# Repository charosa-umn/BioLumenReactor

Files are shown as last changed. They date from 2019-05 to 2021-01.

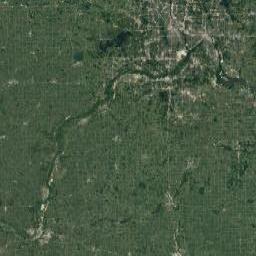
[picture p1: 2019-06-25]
WebPage/Contact_files/embed_data/kh.jpeg

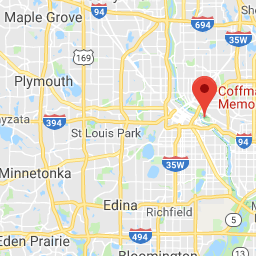
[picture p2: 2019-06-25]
WebPage/Contact_files/embed_data/vt_002.png

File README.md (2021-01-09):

# BioLumen Reactor
The BioLumen Reactor project is dedicated to building a low-cost, small-format bioreactor to culture the bioluminescent bacteria *Vibrio fischeri*. This repository contains open-source code, cell culture protocols, and engineering drawings for the project, and is maintained by **Charosa Research Incubator** at the **University of Minnesota - Twin Cities**.

## Open Source Documentation
- [BioLumen Summary Poster](https://github.com/charosa-umn/BioLumenReactor/blob/master/BioLumen%20Open%20Source%20Files/BioLumen%20Summary%20Poster.pdf)
- [BioLumen Laboratory Manual](https://github.com/charosa-umn/BioLumenReactor/blob/master/BioLumen%20Open%20Source%20Files/BioLumen%20Laboratory%20Manual.pdf)
- [BioLumen Engineering Drawings](https://github.com/charosa-umn/BioLumenReactor/blob/master/BioLumen%20Open%20Source%20Files/BioLumen%20Engineering%20Drawings.pdf)
- [BioLumen Materials List](https://github.com/charosa-umn/BioLumenReactor/blob/master/BioLumen%20Open%20Source%20Files/BioLumen%20Materials%20List.pdf)

## Photos 
BioLumen Reactor
Flask of Vibrio Fischeri

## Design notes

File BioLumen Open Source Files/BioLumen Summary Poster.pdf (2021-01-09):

## Development of a Low-Cost, Small-Format Bioreactor for Bioluminescent Bacterial Cell Culture

David Wang, Conor Sullivan, Joe Herbst, Matthew Landauer, Eric Slaughter, Alex Sweeney Charosa Research Incubator, University of Minnesota

## Introduction

Bioreactors are an essential technology utilized in the production of biologics, fermented products, and specialty chemicals.

[1] Our team seeks to increase exposure to this technology at the undergraduate level. Thus, we have developed a low-cost, small-format bioreactor using nonrestricted materials.
For the demonstration of the bioreactor, the marine bacterium, Vibrio fischeri, was cultured. V. fischeri, which is well-studied for its bioluminescence, is also widely-available for purchase, and is both non-pathogenic and recognized as safe for study in BSL-1 lab spaces.
[2] The bioluminescence of
V. fischeri served crucial for determining inoculation and life cycle timing within the bioreactor system.

## Bioreactor Design

It was critical to the design of the bioreactor that all building materials were widely-available, and that the production of the bioreactor was low-cost in comparison to lab-grade or industrial bioreactors.
The core of the bioreactor is the cell culture vessel, which is a borosilicate glass beaker sealed using a rubber gasket. A magnetic stir plate and stir bar are used to agitate the contents of the vessel. A cylindrical shape for the vessel was chosen for the final design. Initial testing was performed with a round-bottom shape, but issues with stirring turbulence were encountered. The cell culture vessel is modular and can be removed for sterilization separate from the rest of the system. The total volume of the vessel is 1000 mL; considering headspace restrictions during culture, the liquid working volume of the vessel is approximately 500 mL.
The cell-culture vessel is jacketed by a water bath to maintain a consistent temperature. The main structure of the bioreactor system is laser-cut, clear acrylic. Low-cost temperature and pH probes are integrated into the cell culture vessel for real-time monitoring of temperature and pH. A Raspberry Pi 3 microcomputer is used for data output and control of instrumentation.

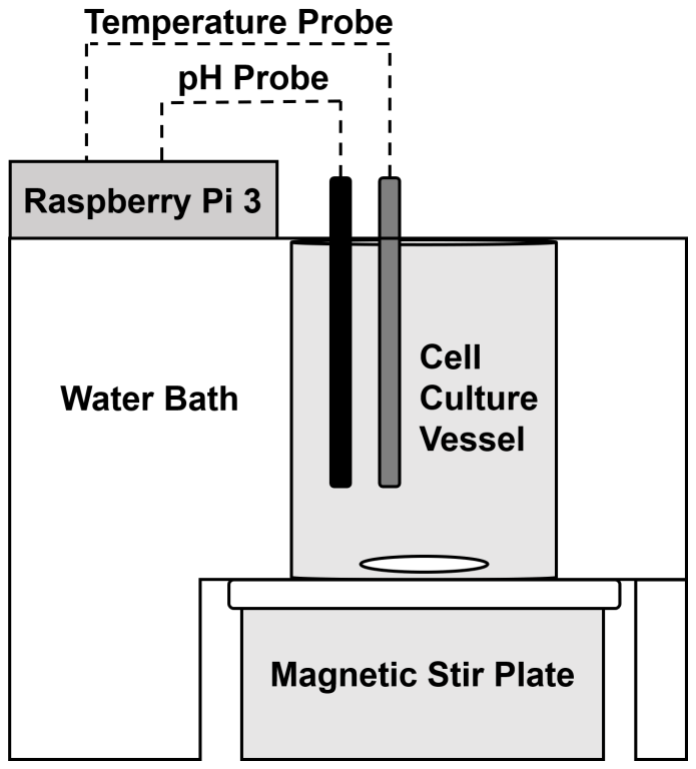
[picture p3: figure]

Figure 1. Final Design Diagram for the Bioreactor

## Cell Culture Methods

The seawater-tryptone nutrient media used for experiments was sourced from the literature and was chosen due to its straightforward composition.

[3] V. fischeri was sourced in the form of educational-grade starter cultures from Carolina Biological Supply Company. Cultures were maintained on solid agar media before scale-up.
For scale-up, 1-2 mL of liquid media was inoculated by a visible cell mass, with 1:10 dilutions of inoculum in fresh nutrient media occurring every 72 hours. Further work to assess scale-up viability was done at the 100 mL scale, with tests done with both shaker platforms and stir plates. Scale-up tests were performed at 22°C, and the target culture pH was approximately 7.2-7.5.
[3] Observed luminescence of the bacteria in culture, which is triggered naturally by cell density, was interpreted as a qualitative indication of both stationary phase growth and of the need for further propagation.

[3]

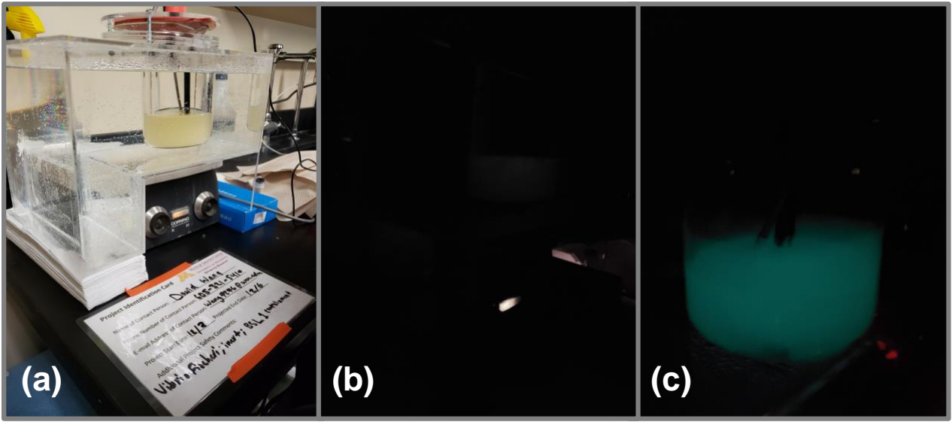
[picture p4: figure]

## Future Directions

- Introduce a heating element for active temperature control; implement a touchscreen and graphical user interface for ease of use
- Pursue other cell culture targets, including hydrogenproducing bacteria, penillicin-producing molds, and cellular viticulture

## Pilot Testing

Test Run 1: The bioreactor was charged with 10% (v/v) inoculum in 500 mL fresh nutrient media. The culture was run for 72 hours. Culture pH and temperature was recorded electronically, but neither parameter was actively controlled. An increase in culture turbidity was observed after 24 hours, but luminescence was not observed during the test run.
Test Run 2: It was suspected that too large of an inoculum volume was used in Test Run 1. Thus, for Test Run 2 the inoculum was reduced to 1% (v/v) in 300 mL fresh nutrient media. The culture was run for 70 hours. After 22 hours the culture turbidity had increased, and after 45 hours luminescence was observed when the culture vessel was shaken.

[1]. Ward, O. P. Bioreactors in Bioprocessing. Bioprocessing 1991, 37–54.
[2]. Ruby et al. Complete Genome Sequence of Vibrio Fischeri: A Symbiotic Bacterium with Pathogenic Congeners. Proc. Natl. Acad. Sci. 2005, 102 (8), 3004–3009. [3]. Madden, D.; Lidesten, B.-M. Bacterial Illumination: Culturing Luminous Bacteria. BioScience Explained 2001.

## References

Figure 2. Test Run 2 at 45 hours: (a) stirred in ambient light,
(b) stirred in total darkness, (c) shaken in total darkness

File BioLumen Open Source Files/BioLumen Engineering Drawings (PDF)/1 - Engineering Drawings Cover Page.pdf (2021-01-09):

# BioLumen Reactor Engineering Drawings

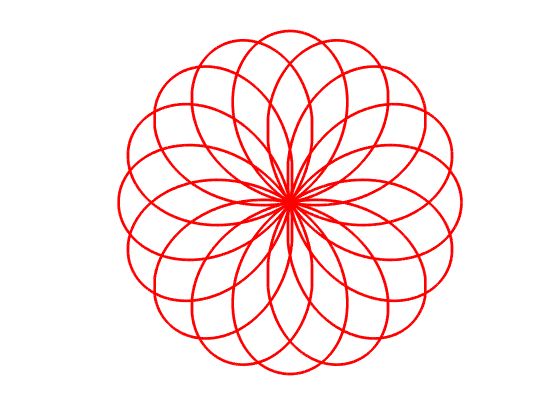
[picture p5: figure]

Author(s): Conor Sullivan
Charosa Research Incubator, University of Minnesota - Twin Cities

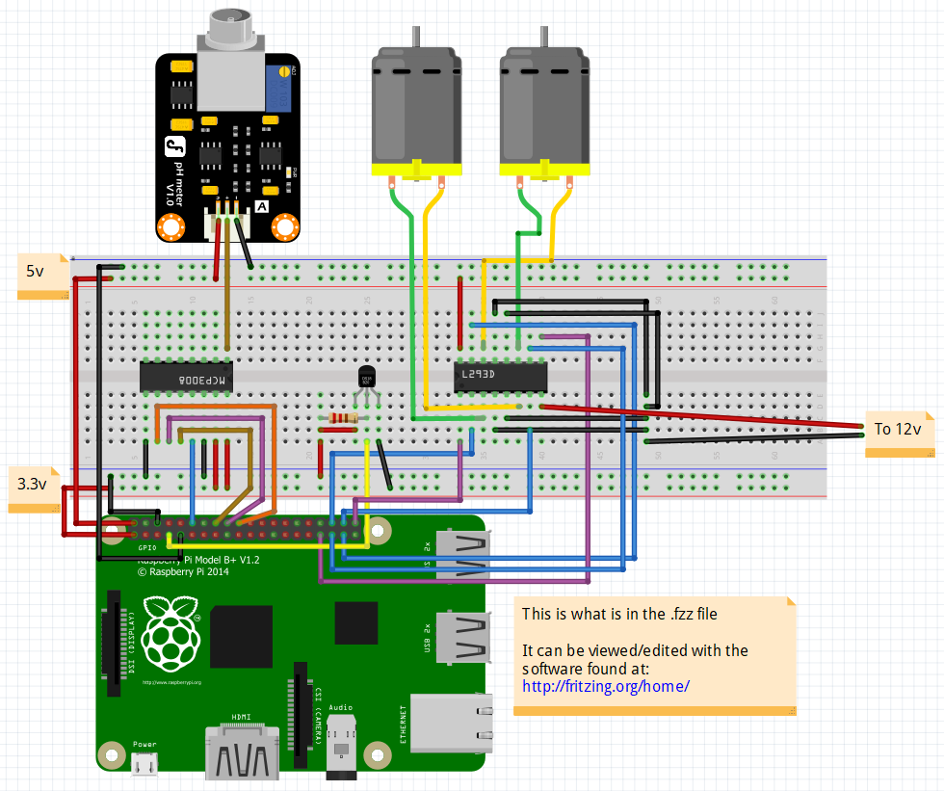
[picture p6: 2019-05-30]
Docs/BoardSchm.png

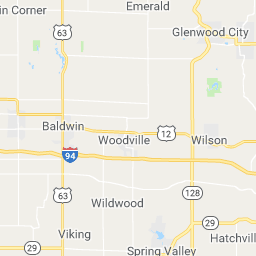
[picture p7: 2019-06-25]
WebPage/Contact_files/embed_data/vt_004.png

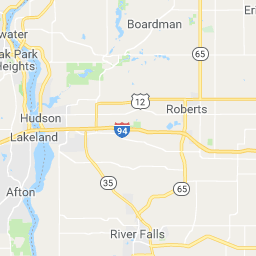
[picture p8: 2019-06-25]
WebPage/Contact_files/embed_data/vt_005.png

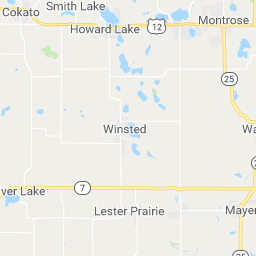
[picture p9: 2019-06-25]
WebPage/Contact_files/embed_data/vt_006.png

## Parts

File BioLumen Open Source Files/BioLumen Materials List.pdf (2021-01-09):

## BioLumen Reactor Materials List

Author(s): David Wang, Conor Sullivan Charosa Research Incubator, University of Minnesota - Twin Cities

Materials for Cell Culture

Item | Recommended Quantity | Preferred Vendor
Magnetic Stir Plate | 1 | eBay
Magnetic Stir Bar | 1 | eBay
Lab Scoopula | 1 | Amazon
Lab Spatula | 1 | Amazon
Digital Milligram Scale | 1 | Amazon
Portable Camp Stove (Flame Source) | 1 | Amazon
Camp Stove Fuel | 1 | Amazon
25 mL Erlenmeyer Flask | 1 | eBay
250 mL Erlenmeyer Flask | 1 | eBay
1 L Media Bottle | 1 | eBay
Plastic Cell Culture Plates | 20 | eBay
Nitrile Gloves | 100 | Amazon
Industrial Spray Bottle | 1 | Amazon
Pressure Cooker | 1 | Amazon
Nichrome Inoculation Loop | 1 | Amazon
Serological Pipette Controller | 1 | eBay

Serological Pipettes | 20 | eBay
Vibrio Fischeri Starter Culture Kit | 1 | Carolina Biological Supply
Yeast Extract | 100 g | Carolina Biological Supply
Seawater Aquarium Salt (‘Instant Ocean’ brand) | 3 lbs | Amazon
Glycerol | 500 mL | Carolina Biological Supply
Tris Base | 250 g | Carolina Biological Supply
Ammonium Chloride | 500 g | Carolina Biological Supply
Tryptone | 500 g | eBay
Calcium Carbonate | 100 g | Carolina Biological Supply
Agar | 100 g | Carolina Biological Supply
Distilled Water | 1 L | Amazon
Ethanol/Isopropanol | 500 mL | Amazon
Clorox Bleach | 1 gal | Amazon

Materials for Construction of Bioreactor

Item | Recommended Quantity | Preferred Vendor
1000 mL Reaction Vessel | 1 | eBay
0.177" thick Acrylic | 32" x 18", 2 sheets | School of Architecture Fab Lab
Acrylic Bonding Agent | 4 oz | Sci-Grip Weld-On 4
Rubber Gasket, ⅛" Thick | 12" x 12", 1 sheet | McMaster Carr, 8525T43
M4x40 Phillips Head BHCS | 4 | -
M4 Wing Nut | 4 | -
Water Heater, 1000 W, 120V | 1 | Denord
Thermocouple/Wire | 1, 3 feet of wire | Amazon
pH sensor | 1 | Amazon
Magnetic Stirrer | 1 | eBay
1" Magnetic Stir Rod | 1 | eBay
Microcontroller | 1 | Raspberry Pi 4

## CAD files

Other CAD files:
BioLumen Open Source Files/BioLumen Engineering Drawings (Source)/ASSY_CLAMPING_RING.iam
BioLumen Open Source Files/BioLumen Engineering Drawings (Source)/ASSY_REACTOR.iam
BioLumen Open Source Files/BioLumen Engineering Drawings (Source)/ASSY_WATER_TANK.iam
BioLumen Open Source Files/BioLumen Engineering Drawings (Source)/BACK_FACE.ipt
BioLumen Open Source Files/BioLumen Engineering Drawings (Source)/BASE.ipt
BioLumen Open Source Files/BioLumen Engineering Drawings (Source)/BOX_SUPPORT.ipt
BioLumen Open Source Files/BioLumen Engineering Drawings (Source)/FRONT_FACE.ipt
BioLumen Open Source Files/BioLumen Engineering Drawings (Source)/GASKET.ipt
BioLumen Open Source Files/BioLumen Engineering Drawings (Source)/GROUND_BASE.ipt
BioLumen Open Source Files/BioLumen Engineering Drawings (Source)/LOWERRING1.ipt
BioLumen Open Source Files/BioLumen Engineering Drawings (Source)/LOWERRING2.ipt
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

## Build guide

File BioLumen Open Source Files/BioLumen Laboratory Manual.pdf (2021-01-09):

## BioLumen Reactor Laboratory Manual

Author(s): David Wang
Charosa Research Incubator, University of Minnesota - Twin Cities

Table of Contents

Introduction | 2
Basic Aseptic Technique for Cell Culture | 3
Alternative Method for Glassware and Reagent Sterilization | 5
Preparation of Photobacterium Liquid and Solid Medium | 7
Subculture of Vibrio Fischeri on Solid Medium | 9
Initiation of Vibrio Fischeri Culture in Liquid Medium | 11
Subculture of Vibrio Fischeri in Liquid Medium | 13
Decontamination of Cell Culture Waste | 15

## Introduction

The goal of the BioLumen Reactor project is to design and build a bioreactor to grow the bioluminescent bacterium Vibrio fischeri. This has required the establishment of multiple laboratory and cell culture protocols that are adaptable to non-standardized working environments, and that are understandable to those with little to no prior laboratory experience. These protocols have been written with reference to prior literature, and also from hands-on experience working with Vibrio fischeri in cell culture. They are also written such that all materials required are non-restricted, and can be freely purchased from sites like eBay, Amazon, and other online retailers.
It is important to note that Vibrio fischeri is a BSL-1 (Biosafety Level 1) organism, meaning it is generally recognized as safe for research, and that it is non-pathogenic to humans. This bacterium exhibits multiple beneficial properties for cell culture, as it is tolerant to a wide range of pH, temperature, and shear conditions in culture. This allows flexibility for culturing at room temperature, with no pH fixing, and with different forms of agitation. It is also commonly used as an educational tool, and so is freely available for purchase at an inexpensive price - in comparison to research-grade strains of bacteria.
This manual represents a year’s worth of laboratory work and literature research by undergraduates at the University of Minnesota - Twin Cities. May it provide you a deeper understanding of cell culture and serve as a future resource for open source science.

David Wang
Project Manager
Charosa Research Incubator

## Basic Aseptic Technique for Cell Culture

Purpose
To remove possible routes of contamination when manipulating cell cultures, and to promote a safe working environment for the cell culturist.

Materials
- Nitrile/latex gloves
- Lab coat (optional)
- Safety glasses (optional)
- Biosafety cabinet (optional)
- Bunsen burner
- 70% ethanol or isopropanol

Procedure
1. Before beginning work, tie long hair up and wash hands thoroughly with soap and water
2. Gown to the appropriate level of personal protective equipment (PPE) for the organism being cultured
a. Gloves are the minimum requirement for PPE
b. Depending on the infection risk of the organism or the necessity for maximum sterility, lab coats, safety glasses or even more stringent PPE may be worn
3. Sterilize the work surface by wiping down thoroughly with 70% ethanol
a. Re-sterilize gloved hands periodically while working with 70% ethanol
b. Similar to Step 2b, a laminar flow hood or biosafety cabinet may be required as an additional layer of protection against contamination and adverse exposure events
c. A non-porous, easily-sterilized work surface in a well-ventilated space is the minimum requirement
4. If working outside of a laminar flow hood or biosafety cabinet, a Bunsen burner can be used to promote a sterile working area (air convection due to flame)
a. Ethanol lamps or butane torches/camp stoves can be used as an alternative to Bunsen burners
b. Avoid rapid gestures when working near a Bunsen burner, and direct coughs or sneezes away from the sterile working area
5. Sterilize any containers or tools that are brought into the sterile area
a. For containers, spray or wipe down openings before use with 70% ethanol
b. For containers, can also ‘flame’ openings before use by slowly moving opening over a Bunsen burner
c. For tools made to be sterilized (glass/steel), can flame sterilize by pouring 95% ethanol over and burning vapors off over a Bunsen burner d. For inoculation loops (nickel/chrome), can flame sterilize directly in a Bunsen burner until glowing orange
e. Let 10 seconds pass after flame sterilizing a tool before use, and do not bring tool into contact with non-sterile surfaces in the interim
6. When finished working, re-sterilize the work surface with 70% ethanol and wash hands thoroughly with soap and water

References
1. Coté, R. Aseptic Technique For Cell Culture. Current Protocols in Cell Biology 1998, 00 (1), 1.3.1-1.3.10.
2. Cell Culture Protocol 1: Proper Aseptic Technique and Sterile Handling of Cells. https://www.sigmaaldrich.com/technical-documents/protocols/biology/aseptic-technique. html (accessed Aug 17, 2020).

## Alternative Method for Glassware and Reagent Sterilization

Purpose
To ensure that all glassware, media, and other components that come into contact with a culture are properly sterilized before use.

Materials
- Pressure Cooker or Autoclave (recommended)
- Liquid Medium/Agar/Glassware to sterilize

Procedure
1. If using an autoclave, see manufacturer instructions for most accurate guidance.
a. Generally use a ‘liquid cycle’ if available for liquid media
b. For agar/agarose gels, cycle times > 20 minutes are recommended
c. Do not fill your container more than half of its total volume with liquid, to prevent over-pressurization
d. Ensure a layer of secondary containment when autoclaving, i.e. an autoclave-safe tray or bin
e. For vessels or bottles filled with liquid, make sure caps are screwed on loosely, to prevent over-pressuring the container
f. It is recommended to use autoclave tape on the vessel of interest, which changes color to ensure that the autoclave reached the proper temperature
2. If using a pressure cooker, set so as to maintain 15 psi for > 15 minutes
a. An inch or two of water in the pressure cooker vessel is necessary for steam pressurization
b. Set containers offset from the bottom of the pressure cooker vessel, to prevent overheating
c. Do not fill your container more than half of its total volume with liquid, to prevent overpressurization
d. For vessels or bottles filled with liquid, make sure caps are screwed on loosely, to prevent over-pressuring the container
e. It is recommended to let steam vent naturally, rather than directly releasing steam via a pressure cooker’s depressurization valve after a pressure cycle
f. A foil cap, taped over the container can be substituted if a vessel does not have a built-in cap
3. After sterilizing a container, do not open or expose its contents unless in a sterile environment
a. Either a biosafety cabinet, laminar flow hood, or sterile field provided by a Bunsen burner

References
1. Teach.Genetics. 2015. Sterilizing Liquids. [online] Available at: <https://teach.genetics.utah.edu/content/microbiology/liquids/> [Accessed 19 August 2020].
2. Swenson, V.; Stacy, A.; Gaylor, M.; Ushijima, B.; Philmus, B.; Cozy, L.; Videau, N.; Videau, P. Assessment And Verification Of Commercially Available Pressure Cookers For Laboratory Sterilization. PLOS ONE 2018, 13 (12), e0208769.

## Preparation of Photobacterium Liquid and Solid Medium

Purpose
To prepare both liquid and solid growth medium for the culture of Vibrio fischeri or other photobacterium.

Materials
- Seawater aquarium salt (33 g/L)
- Yeast extract (5 g/L)
- Tryptone (5 g/L)
- Glycerol (3 g/L, ~2.5–3 mL)
- Tris (6 g/L)
- NH4Cl (5 g/L)
- Distilled water
- CaCO3 (1 g/L, for solid medium)
- Agar (15–20 g/L, for solid medium)
- Erlenmeyer flask/media bottle
- Plastic cell culture plates or sterile glass petri dishes (for solid medium)
Procedure
1. Measure the required solids for liquid medium, and transfer to a suitable container for autoclaving and pouring (Erlenmeyer flask/media bottle)
a. If preparing solid medium, measure the additional solids, CaCO3 and agar, to supplement the liquid recipe
2. Dissolve the solids in the desired volume of distilled water, and add liquid glycerol
a. Small amount of solids may not completely dissolve at room temperature, can move forward if solution is nearly clear
3. Autoclave or pressure sterilize, a cycle time > 20 minutes is recommended
a. See ‘Alternative Method for Glassware and Reagent Sterilization’
4. Allow solution to cool to a manageable temperature, ~15-20 minutes
a. If preparing liquid medium, once cooled can store refrigerated for 3-4 weeks or longer if kept sterile
5. If preparing solid medium, set up a sterile work area to pour agar plates
a. See ‘Basic Aseptic Technique for Cell Culture’, Steps 1-4
6. Pour plates within the sterile work area
a. Set plates on sterile work surface and pour agar down from container
b. Keep one hand free to move plate lids, and use the other to pour liquid agar from the container
c. Only need to pour enough to cover the bottom of the plate
d. Replace place lid, slightly askew, after pouring agar
e. Allow excess steam to be released, ~15-20 minutes, before properly closing plate lids and storing plates f. Store plates upside down, agar-side up, to prevent condensation forming on the agar surface
g. Can store plates either in plastic-wrapped stacks or in the plastic sleeves that they originally came in
h. Plates can be stored refrigerator for 3-4 weeks or longer if kept sterile, and if the agar has not dried out
7. Re-sterilize the work area and work tools; clear the work area and put away items used for the procedure

References
1. Madden, D. and Lidesten, B., 2001. Bacterial Illumination. [online] Available at: <https://bioenv.gu.se/digitalAssets/1566/1566430_photoen.pdf> [Accessed 24 August 2020].
2. Making Agar Plates. https://teach.genetics.utah.edu/content/microbiology/plates/(accessed Aug 24, 2020).

## Subculture of Vibrio Fischeri on Solid Medium

Purpose
To promote the aseptic subculturing of Vibrio fischeri from a starter culture on solid medium to another solid medium.

Materials
- Inoculation loop
- Starter culture, on agar slant/plate
- Bunsen burner or alternative
- 70% ethanol
- Photobacterium agar plate

Procedure
1. Prepare a sterile work area with the Bunsen burner and by wiping down work surfaces with 70% ethanol
a. See Basic Aseptic Technique for Cell Culture, Steps 1-4
2. Move all containers and working items into the sterile work area
a. See Basic Aseptic Technique for Cell Culture, Step 5
3. Flame sterilize inoculation loop in Bunsen burner before contact with any culture
a. See Basic Aseptic Technique for Cell Culture, Step 5
4. Work carefully, using one hand to manipulate the inoculation loop, and one hand to manipulate the cell cultures
5. Rub inoculation loop over an area of the starter culture surface with visible bacteria growth
a. Can look like white or yellow ‘plaques’ on the agar
b. Can confirm if the visible areas are Vibrio fischeri growth by viewing them in a dark room to check bioluminescence - should glow blue-green
6. Without touching the inoculated loop to any other surface, rub the loop onto the surface of the fresh agar plate
a. Recommended technique is to ‘streak’ from center to rim of the plate
b. Very little force is necessary to streak the plate with the inoculation loop, be careful not to tear the agar
c. See Reference 1 for more information on plating techniques
7. Label plate lid with a Sharpie or other indelible marker, noting the date of subculture, the organism name, the type of medium, and the name of the cell culturist
8. Let plate incubate at the appropriate temperature, light intensity, and humidity
a. For Vibrio fischeri, average room temperature (~22° C) or slightly below is an appropriate temperature, and store in a dark, dry space to incubate
9. Re-sterilize the work area and work tools; clear the work area and put away items used for the procedure

10. Depending on how effective the inoculation from the starter culture was, bioluminescence of the culture on solid medium can be observed after ~24 hours
a. Observe in a dark room, and give time for eyesight to adjust to the dark before viewing

References
1. Sanders, E. Aseptic Laboratory Techniques: Plating Methods. Journal of Visualized Experiments 2012, No. 63.

## Initiation of Vibrio Fischeri Culture in Liquid Medium

Purpose
To promote the aseptic subculturing of Vibrio fischeri from a starter culture on solid medium to liquid medium.

Materials
- Inoculation loop
- Starter culture, on agar slant/plate
- Bunsen burner or alternative
- 70% ethanol
- Photobacterium liquid medium
- Cell culture flask (Shake flask/Erlenmeyer flask)
- Magnetic stir plate/shaker platform
- Magnetic stir bar

Procedure
1. Prepare a sterile work area with the Bunsen burner and by wiping down work surfaces with 70% ethanol
a. See Basic Aseptic Technique for Cell Culture, Steps 1-4
2. Move all containers and working items into the sterile work area
a. See Basic Aseptic Technique for Cell Culture, Step 5
3. Flame sterilize inoculation loop in Bunsen burner before contact with any culture
a. See Basic Aseptic Technique for Cell Culture, Step 5
4. Prepare the cell culture flask (sterilized shake/Erlenmeyer flask) by filling with liquid medium
a. If using a magnetic stir plate, insert a magnetic stir bar into the cell culture flask
b. If using an Erlenmeyer flask without a lid, use a metal foil cap (secured with tape) to cover the opening before taking the flask out of the sterile region
c. Do not fill the cell culture flask beyond half of its indicated volume, to ensure excess oxygen headspace for the culture
d. The smaller the volume of media, the faster it will take for the seed culture of Vibrio fischeri to deplete the media of nutrients and begin to die off; 15-20 mL of liquid media for the initiation is recommended
5. Work carefully, using one hand to manipulate the inoculation loop, and one hand to manipulate the cell cultures
6. Rub inoculation loop over an area of the starter culture surface with visible bacteria growth
a. Can look like white or yellow ‘plaques’ on the agar
b. Can confirm if the visible areas are Vibrio fischeri growth by viewing them in a dark room to check bioluminescence - should glow blue-green c. To ensure enough transfer of cells, scrape enough cells to notice visually from the surface of the plate
7. Without touching the inoculated loop to any other surface, insert the loop below the liquid surface of the cell culture flask and swirl/shake the loop to inoculate the medium with seed cells
a. Swirling the inoculation loop in the liquid medu only requires ~15 seconds
b. If a visible cell mass was scraped from the starter culture, shake until dislodged from the inoculation loop
8. Reseal the cell culture flask, and incubate at the appropriate temperature, light intensity, and humidity on either a magnetic stir plate or shaker platform
a. For Vibrio fischeri, average room temperature (~22° C) or slightly below is an appropriate temperature, and store in a dark, dry space to incubate
b. To determine a proper agitation rate for shaker or stir plate in the case that the culture was inoculated with a visible cell mass, choose a high enough rate to visibly rotate the cell mass at > 1/second.
9. Re-sterilize the work area and work tools; clear the work area and put away items used for the procedure
10. Depending on the volume of media in the cell culture flask and how large the inoculation mass was, bioluminescence of the liquid culture can be observed after ~24 hours, and can be induced by shaking the culture flask, assuming excess oxygen headspace for the culture
a. Observe in a dark room, and give time for eyesight to adjust to the dark before viewing

References
1. Christensen, D. and Visick, K., 2020. Vibrio fischeri : Laboratory Cultivation, Storage, and Common Phenotypic Assays. Current Protocols in Microbiology, 57(1).
2. Living Organism Care Guide: Vibrio fischeri. https://www.carolina.com/teacher-resources/Interactive/living-organism-care-guide-vibrio-fischeri/tr23902.tr (accessed Aug 29, 2020).

## Subculture of Vibrio Fischeri in Liquid Medium

Purpose
To promote the aseptic subculturing of Vibrio fischeri from a starter culture in liquid medium to another liquid medium.

Materials
- Serological pipette/pipette gun
- Starter culture, in liquid medium
- Bunsen burner or alternative
- 70% ethanol
- Photobacterium liquid medium
- Cell culture flask (Shake flask/Erlenmeyer flask)
- Magnetic stir plate/shaker platform
- Magnetic stir bar (if using stir plate)

Procedure
1. Prepare a sterile work area with the Bunsen burner and by wiping down work surfaces with 70% ethanol
a. See Basic Aseptic Technique for Cell Culture, Steps 1-4
2. Move all containers and working items into the sterile work area
a. See Basic Aseptic Technique for Cell Culture, Step 5
3. Prepare the cell culture flask (sterilized shake/Erlenmeyer flask) by filling with liquid medium
a. If using a magnetic stir plate, insert a magnetic stir bar into the cell culture flask
b. If using an Erlenmeyer flask without a lid, use a metal foil cap (secured with tape) to cover the opening before taking the flask out of the sterile region
c. Do not fill the cell culture flask beyond half of its indicated volume, to ensure excess oxygen headspace for the culture
d. The chosen volume of liquid medium for the subculture vessel depends on multiple factors:
i. If expansion of the cell culture is desired, the entire starter culture can be transferred into a much larger volume of fresh cell culture media
ii. | If the total volume of the culture is meant to be conserved, a fractional
| volume of the starter culture can be transferred into a proportional volume
| of fresh cell culture media
iii. | A volume ratio of 1:100 starter culture to fresh media is recommended for
| cell culture expansion, to maintain ~3 day growth cycle
4. Using a serological pipette and pipette gun, transfer the intended volume of active culture from the starter culture flask to the fresh medium flask
a. Before transferring liquid from the starter culture flask to the serological pipette, swirl the flask to resuspend and homogenize the cells in the culture medium b. Do not contaminate the outer surface of the serological pipette by touching to any other surface while transferring the cell culture liquid
c. If a serological pipette and pipette gun is not available, it is possible to pour starter culture liquid from one flask to another; however, this increases the risk of contamination by the surrounding air, and increases the risks of spills
5. Reseal the new cell culture flask, and incubate at the appropriate temperature, light intensity, and humidity on either a magnetic stir plate or shaker platform
a. For Vibrio fischeri, average room temperature (~22° C) or slightly below is an appropriate temperature, and store in a dark, dry space to incubate
b. To determine a proper agitation rate for shaker or stir plate in the case that the culture was inoculated with a visible cell mass, choose a high enough rate to visibly rotate the cell mass at > 1/second.
6. Re-sterilize the work area and work tools; clear the work area and put away items used for the procedure
7. Depending on the volume of media in the cell culture flask and how large the inoculation volume was, bioluminescence of the liquid culture can be observed after ~24 hours, and can be induced by shaking the culture flask, assuming excess oxygen headspace for the culture
a. Observe in a dark room, and give time for eyesight to adjust to the dark before viewing

References
1. Christensen, D. and Visick, K., 2020. Vibrio fischeri : Laboratory Cultivation, Storage, and Common Phenotypic Assays. Current Protocols in Microbiology, 57(1).
2. Living Organism Care Guide: Vibrio fischeri. https://www.carolina.com/teacher-resources/Interactive/living-organism-care-guide-vibrio-fischeri/tr23902.tr (accessed Aug 29, 2020).

## Decontamination of Cell Culture Waste

Purpose
To safely decontaminate and dispose of cell culture wastes - most importantly, spent cell culture medium used for the growth of Vibrio fischeri.

Materials
- Clorox Bleach (NaOCl)
- Cell Culture Waste
- Autoclave (or equivalent)

Procedure
1. For decontamination of cell cultures in liquid medium with bleach, dilute until flask contains 10% bleach by volume
a. If possible, perform decontamination procedure within a fume hood or other well-vented area
b. Allow at least 20 minutes of contact time for bleach in solution to inactivate any cells left in the culture
c. Can dispose of decontaminated solution via drain disposal, flushed down with copious amounts of water
2. For decontamination of cell cultures on solid medium with bleach, can prepare a solution of 10% bleach in water in a large bin
a. Submerge cell culture plates, or other solid growth media fully under bleach solution
b. Allow at least 20 minutes of contact time for bleach in solution to inactivate any cells left in the culture
c. Can dispose of decontaminated solids as biohazard waste in accordance with institutional or local guidelines
3. For decontamination of cell cultures in liquid or solid medium in an autoclave or equivalent:
a. Place cell culture flasks/plates in a leakproof, autoclave-safe bin
b. Ensure that any containers with liquid are no more than half full
c. Autoclave as recommended by machine instructions; see Alternative Method for Glassware and Reagent Sterilization for more information
d. Can dispose of decontaminated liquids via drain disposal, flushed down with copious amounts of water
e. Can dispose of decontaminated solids as biohazard waste in accordance with institutional or local guidelines

References
1. COMS Policy on Suitable Methods of Liquid Decontamination and Disposal. https://hms.harvard.edu/departments/committee-microbiological-safety/registering-coms/coms-policies/coms-policy-suitable-methods-liquid-decontamination-disposal (accessed Aug 31, 2020).
2. COMS Policy on Suitable Methods of Liquid Decontamination and Disposal. https://hms.harvard.edu/departments/committee-microbiological-safety/registering-coms/coms-policies/coms-policy-suitable-methods-liquid-decontamination-disposal (accessed Aug 31, 2020).

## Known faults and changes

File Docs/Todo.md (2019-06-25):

### TODO List for BioLumen

Things that need to be decided/done:

- [x] What we will use for the controller
- [x] What language we will be using
- [x] Board schimatic
- [x] What sensors we will need
- [x] Set up temp reading
- [x] Convert volatage from digital to pH
- [x] Writting to csv
- [x] Write to realtime webpage
- [x] Display realtime graph
- [x] Begin after button press
- [x] Prep routine
- [ ] Run on startup
- [ ] Get data file to mounted flashdrive
- [ ] Calibrating pH sensor
- [ ] Power down when off switch is activated
- [ ] Begin prep when on switch is activated
- [ ] Documentation requirements

Items that we WILL need:
- [x] RaspberryPi
- [x] Resistors
- [x] Thermometer sensor
- [x] ph sensor
- [x] Breadboard
- [x] Pump for acids and bases
- [ ] Wires
- [ ] PCB board
- [ ] On/off switch
- [ ] Push button

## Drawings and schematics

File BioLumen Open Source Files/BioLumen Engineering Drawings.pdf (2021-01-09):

# BioLumen Reactor Engineering Drawings


Author(s): Conor Sullivan
Charosa Research Incubator, University of Minnesota - Twin Cities

1

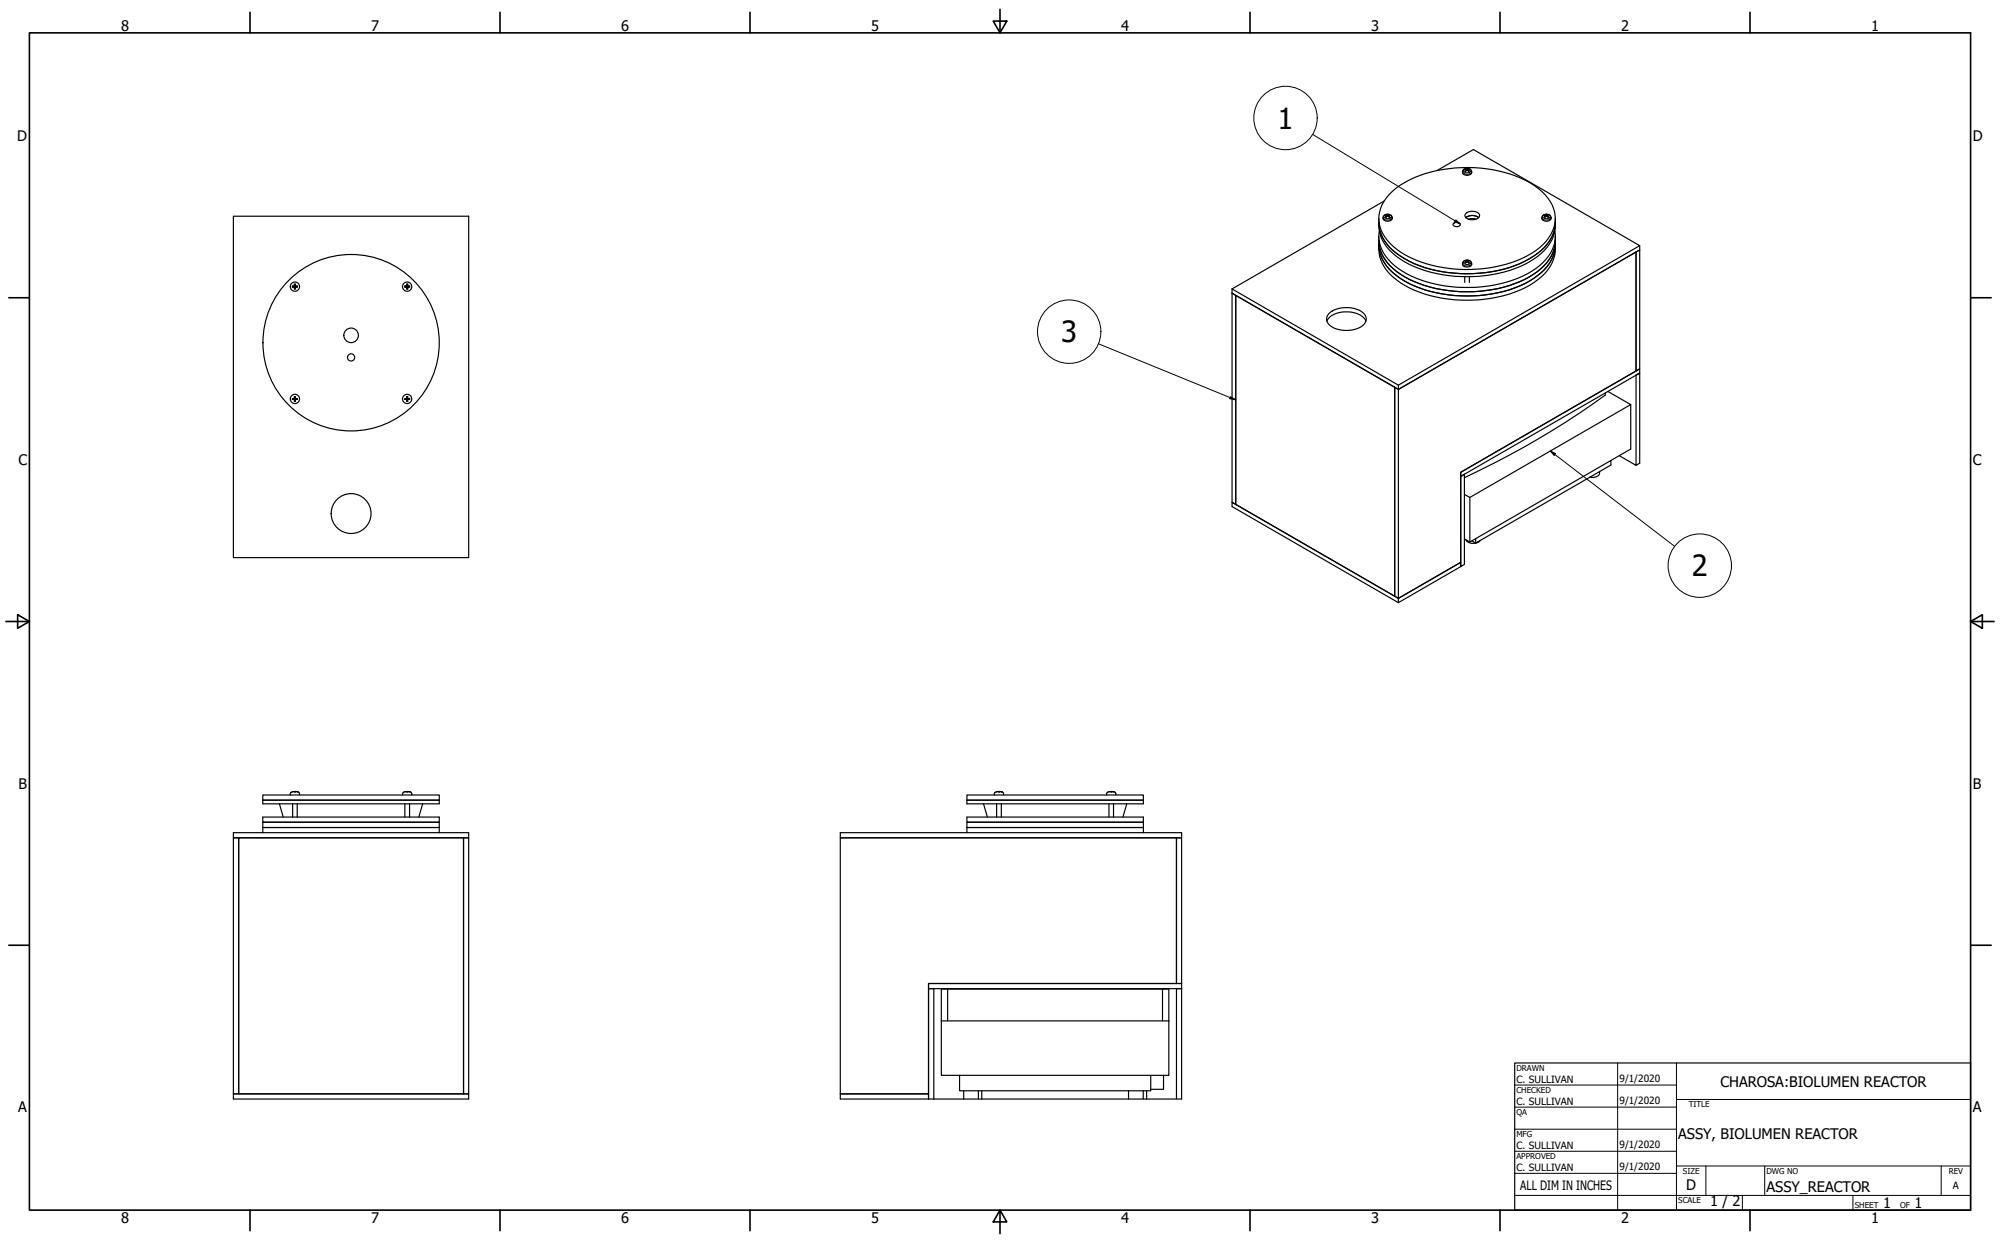
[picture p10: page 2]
SHEET 1 OF 1; DRAWN; CHECKED; C. SULLIVAN; DWG NO; ASSY_REACTOR; TITLE; SIZE D; SCALE; REV A

CHAROSA:BIOLUMEN REACTOR

ASSY, BIOLUMEN REACTOR

MFG
C. SULLIVAN
APPROVED
ALL DIM IN INCHES

3

6

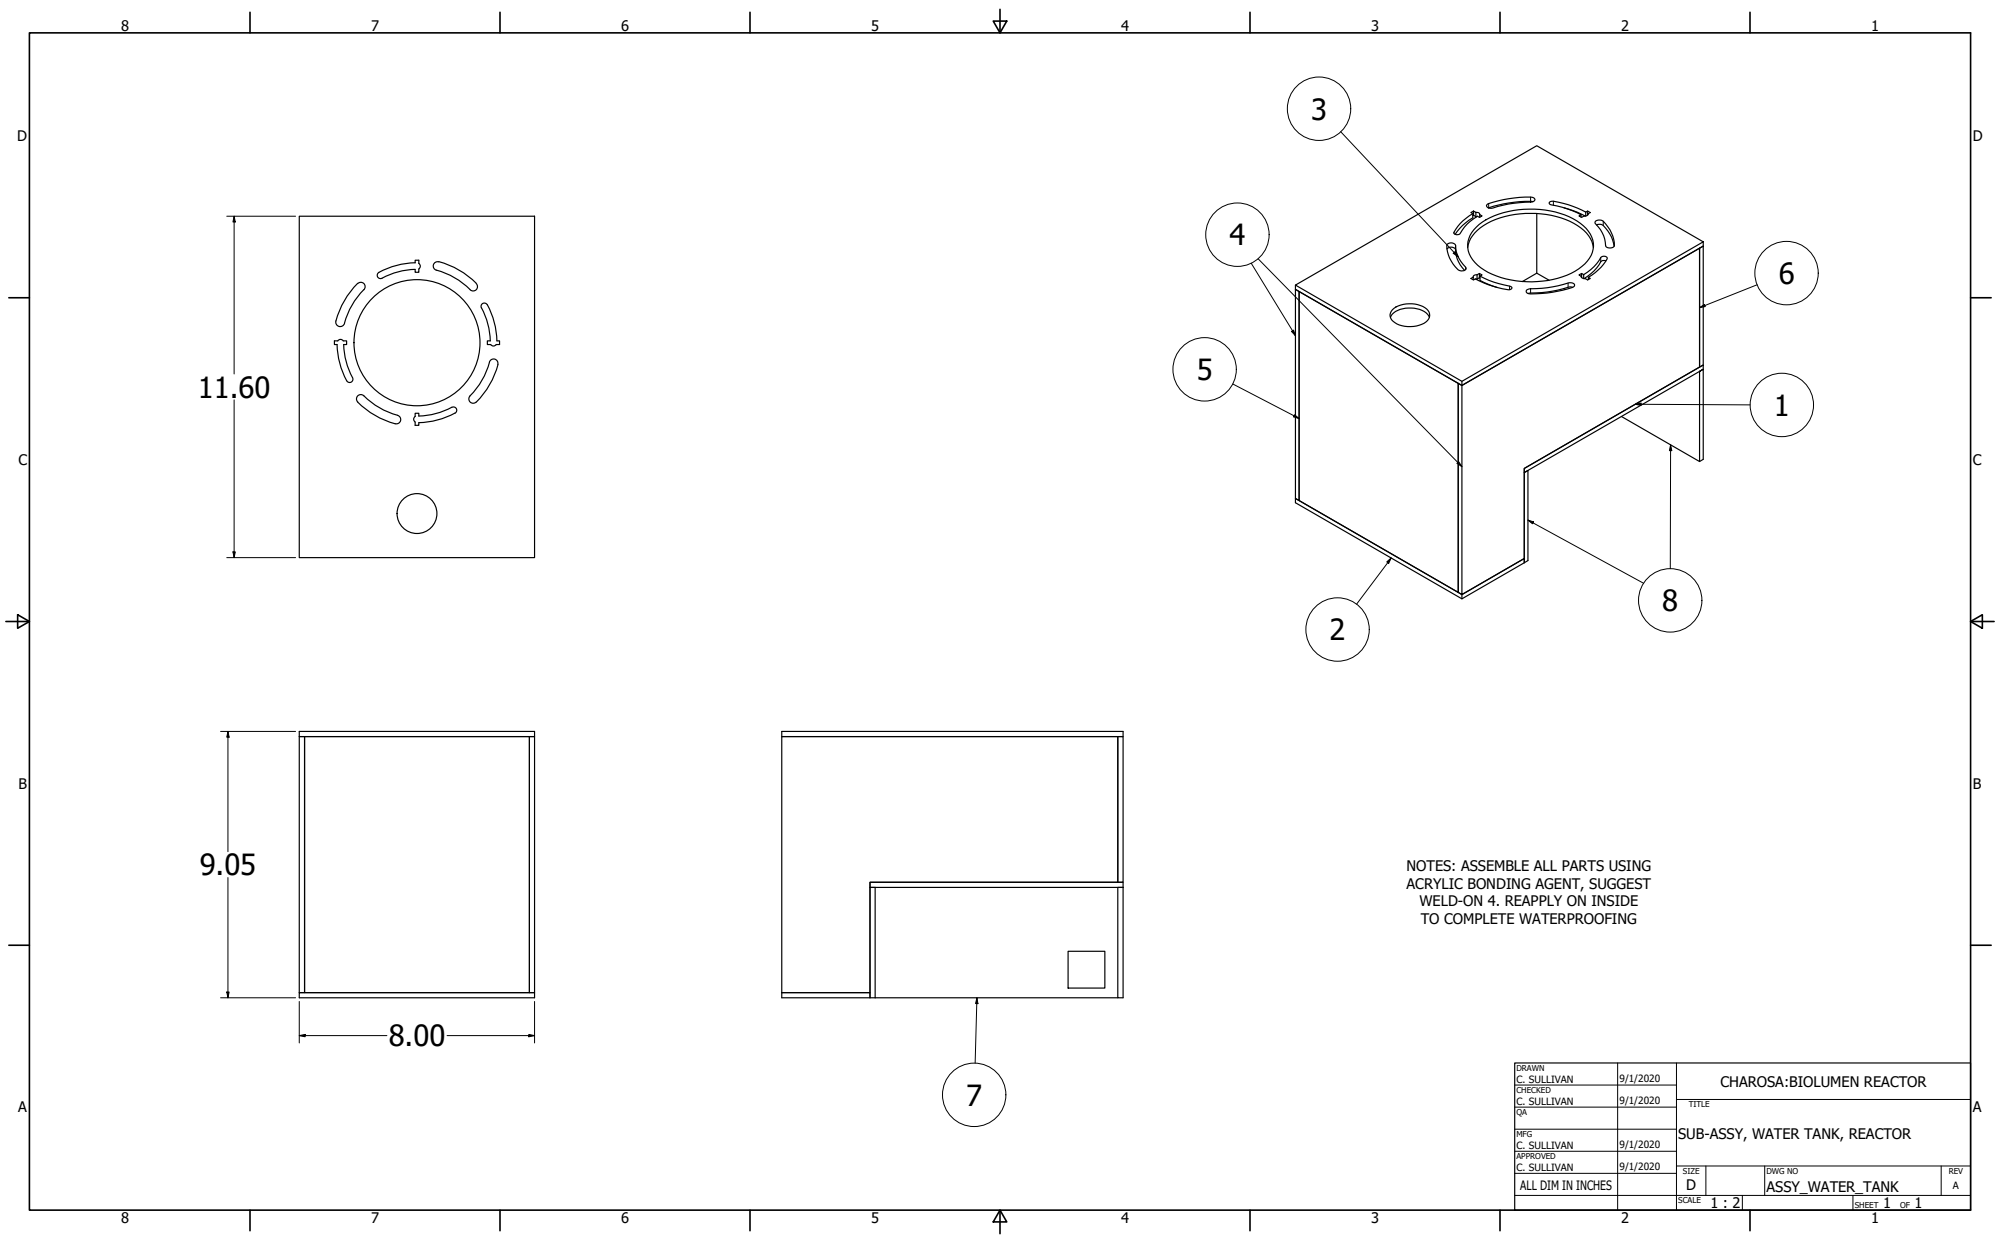
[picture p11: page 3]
DRAWN; CHECKED; MFG C. SULLIVAN; C. SULLIVAN; ASSY_WATER_TANK; TITLE

NOTES: ASSEMBLE ALL PARTS USING
ACRYLIC BONDING AGENT, SUGGEST
WELD-ON 4. REAPPLY ON INSIDE
TO COMPLETE WATERPROOFING

CHAROSA:BIOLUMEN REACTOR

SUB-ASSY, WATER TANK, REACTOR

8 11

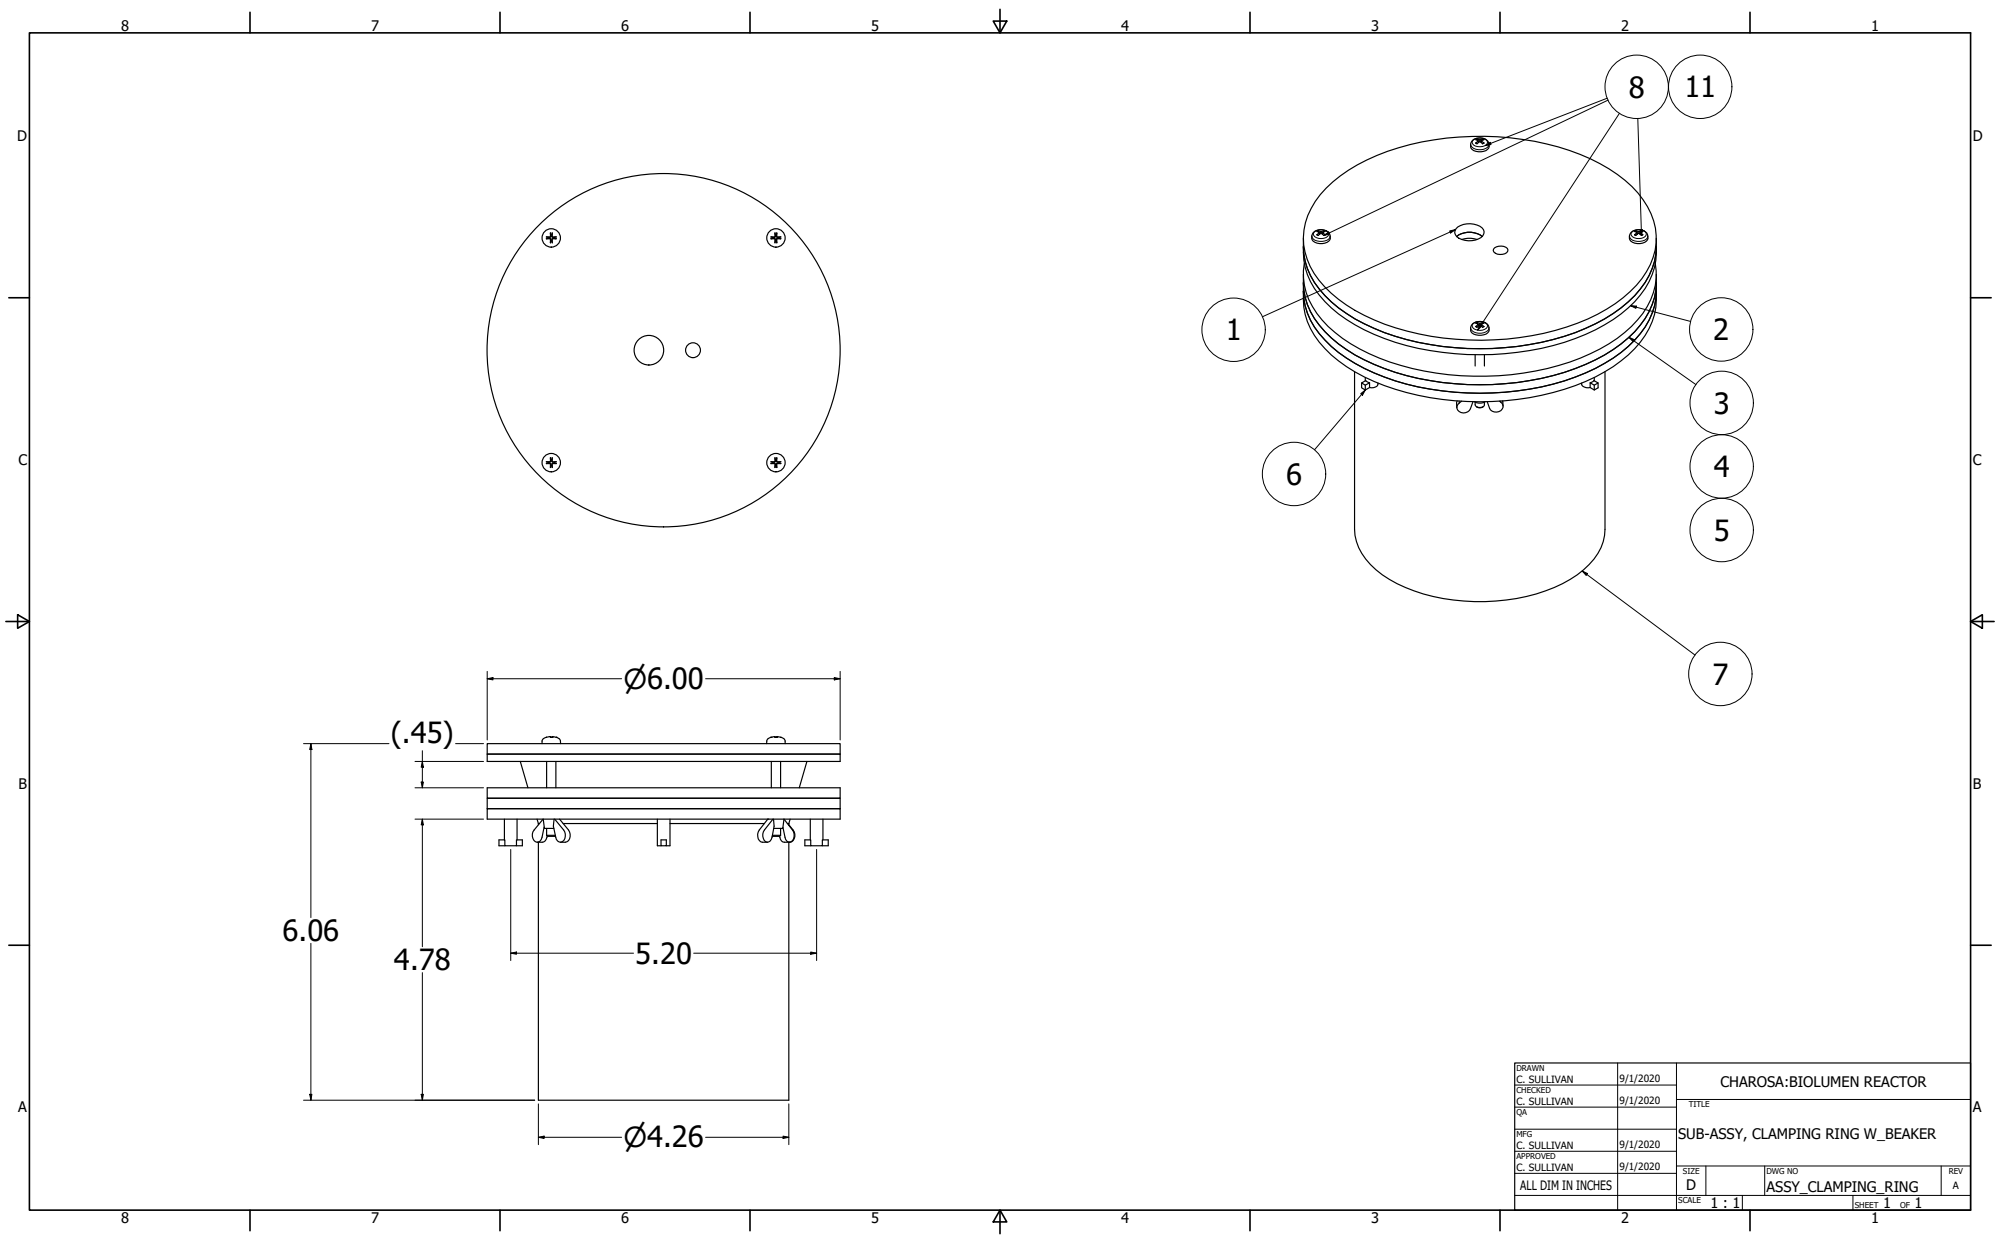
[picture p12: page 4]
DRAWN; CHECKED; MFG C. SULLIVAN; C. SULLIVAN; ASSY_CLAMPING_RING; TITLE

CHAROSA:BIOLUMEN REACTOR

SUB-ASSY, CLAMPING RING W_BEAKER

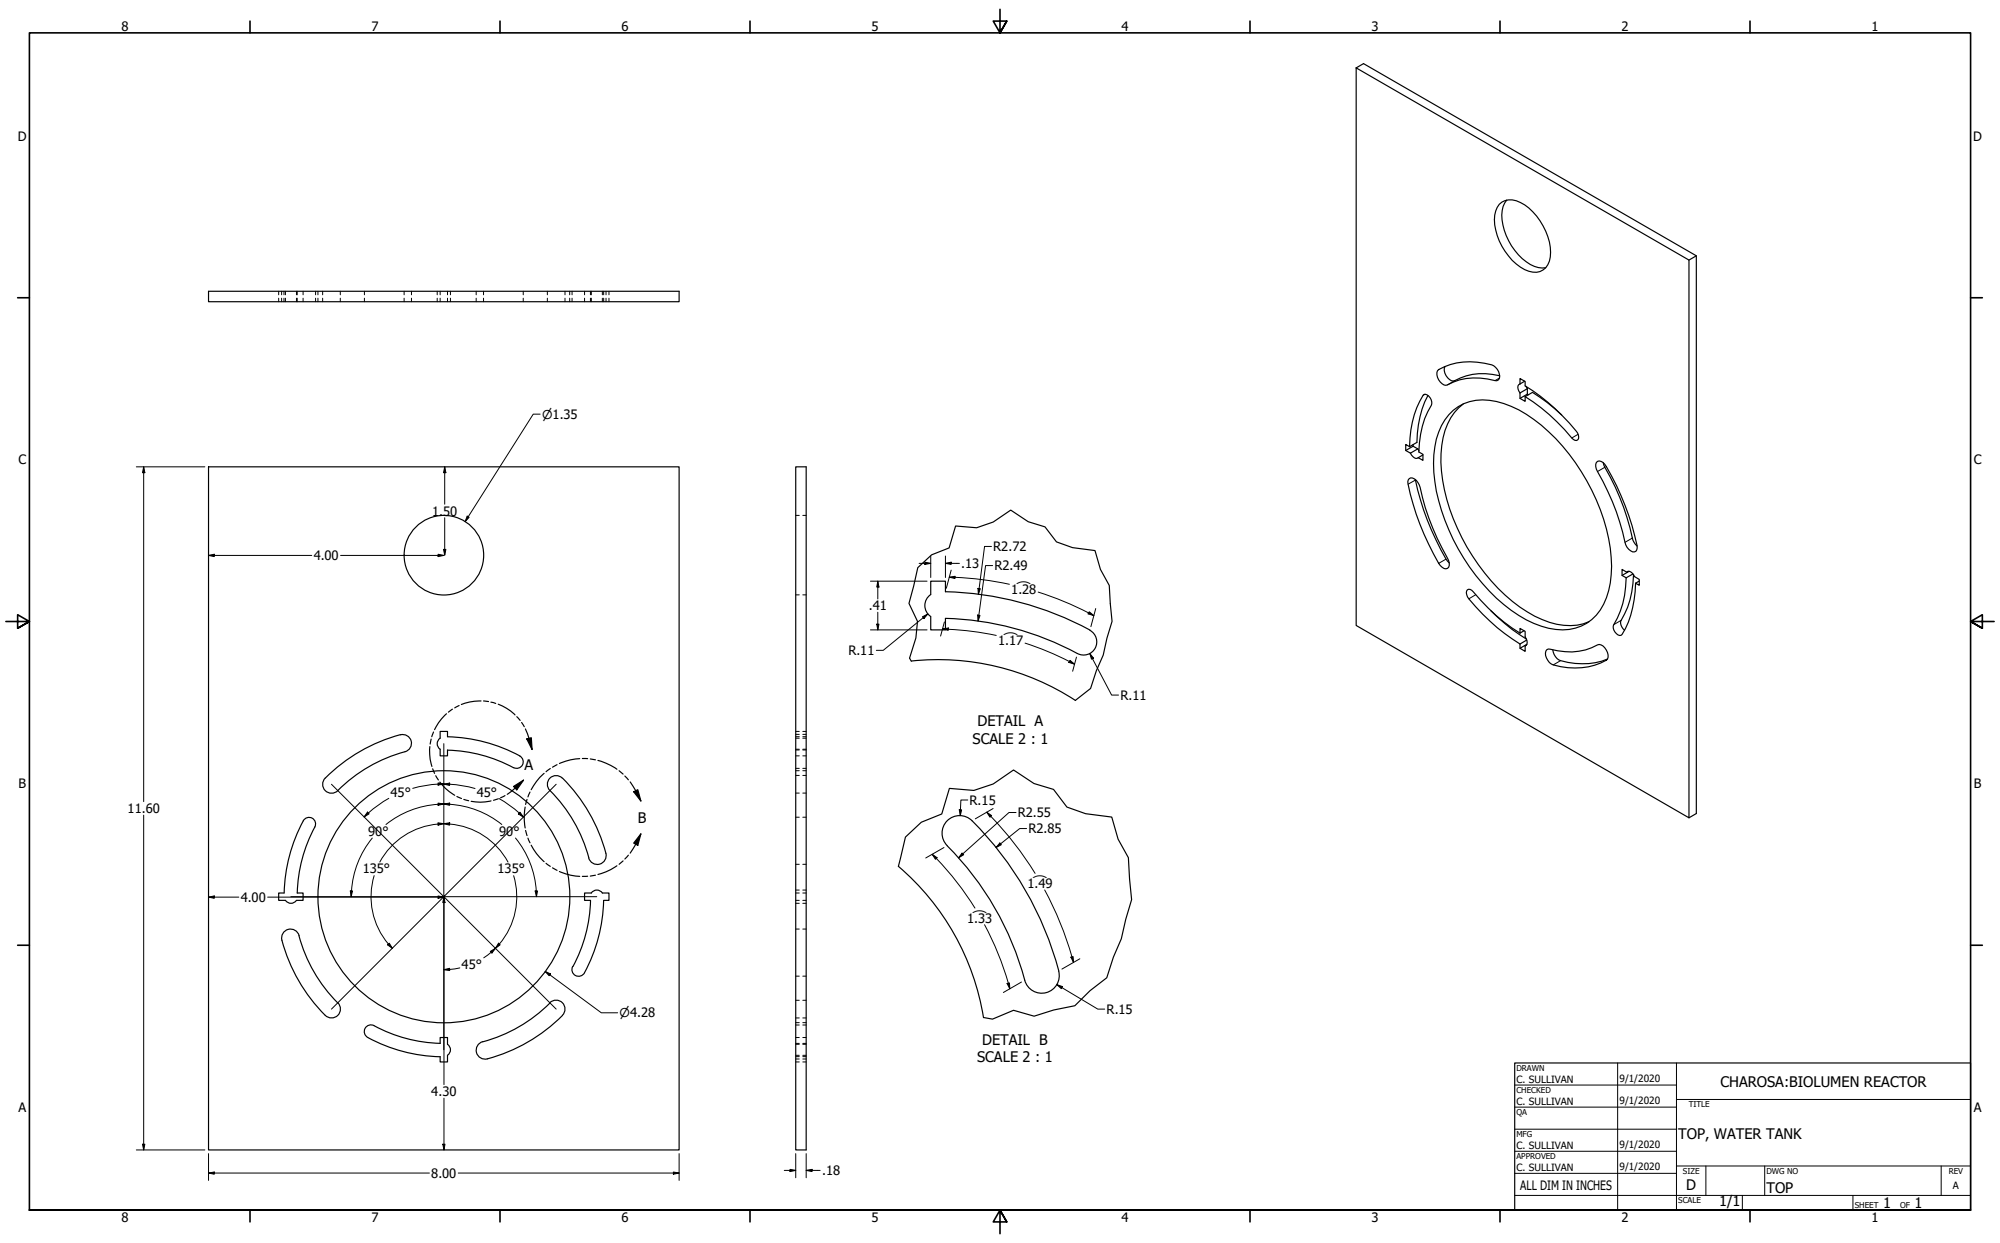
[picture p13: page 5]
DETAIL A SCALE 2 : 1; DETAIL B SCALE 2 : 1; DRAWN; CHECKED; MFG C. SULLIVAN; C. SULLIVAN; TOP; TITLE

CHAROSA:BIOLUMEN REACTOR

TOP, WATER TANK

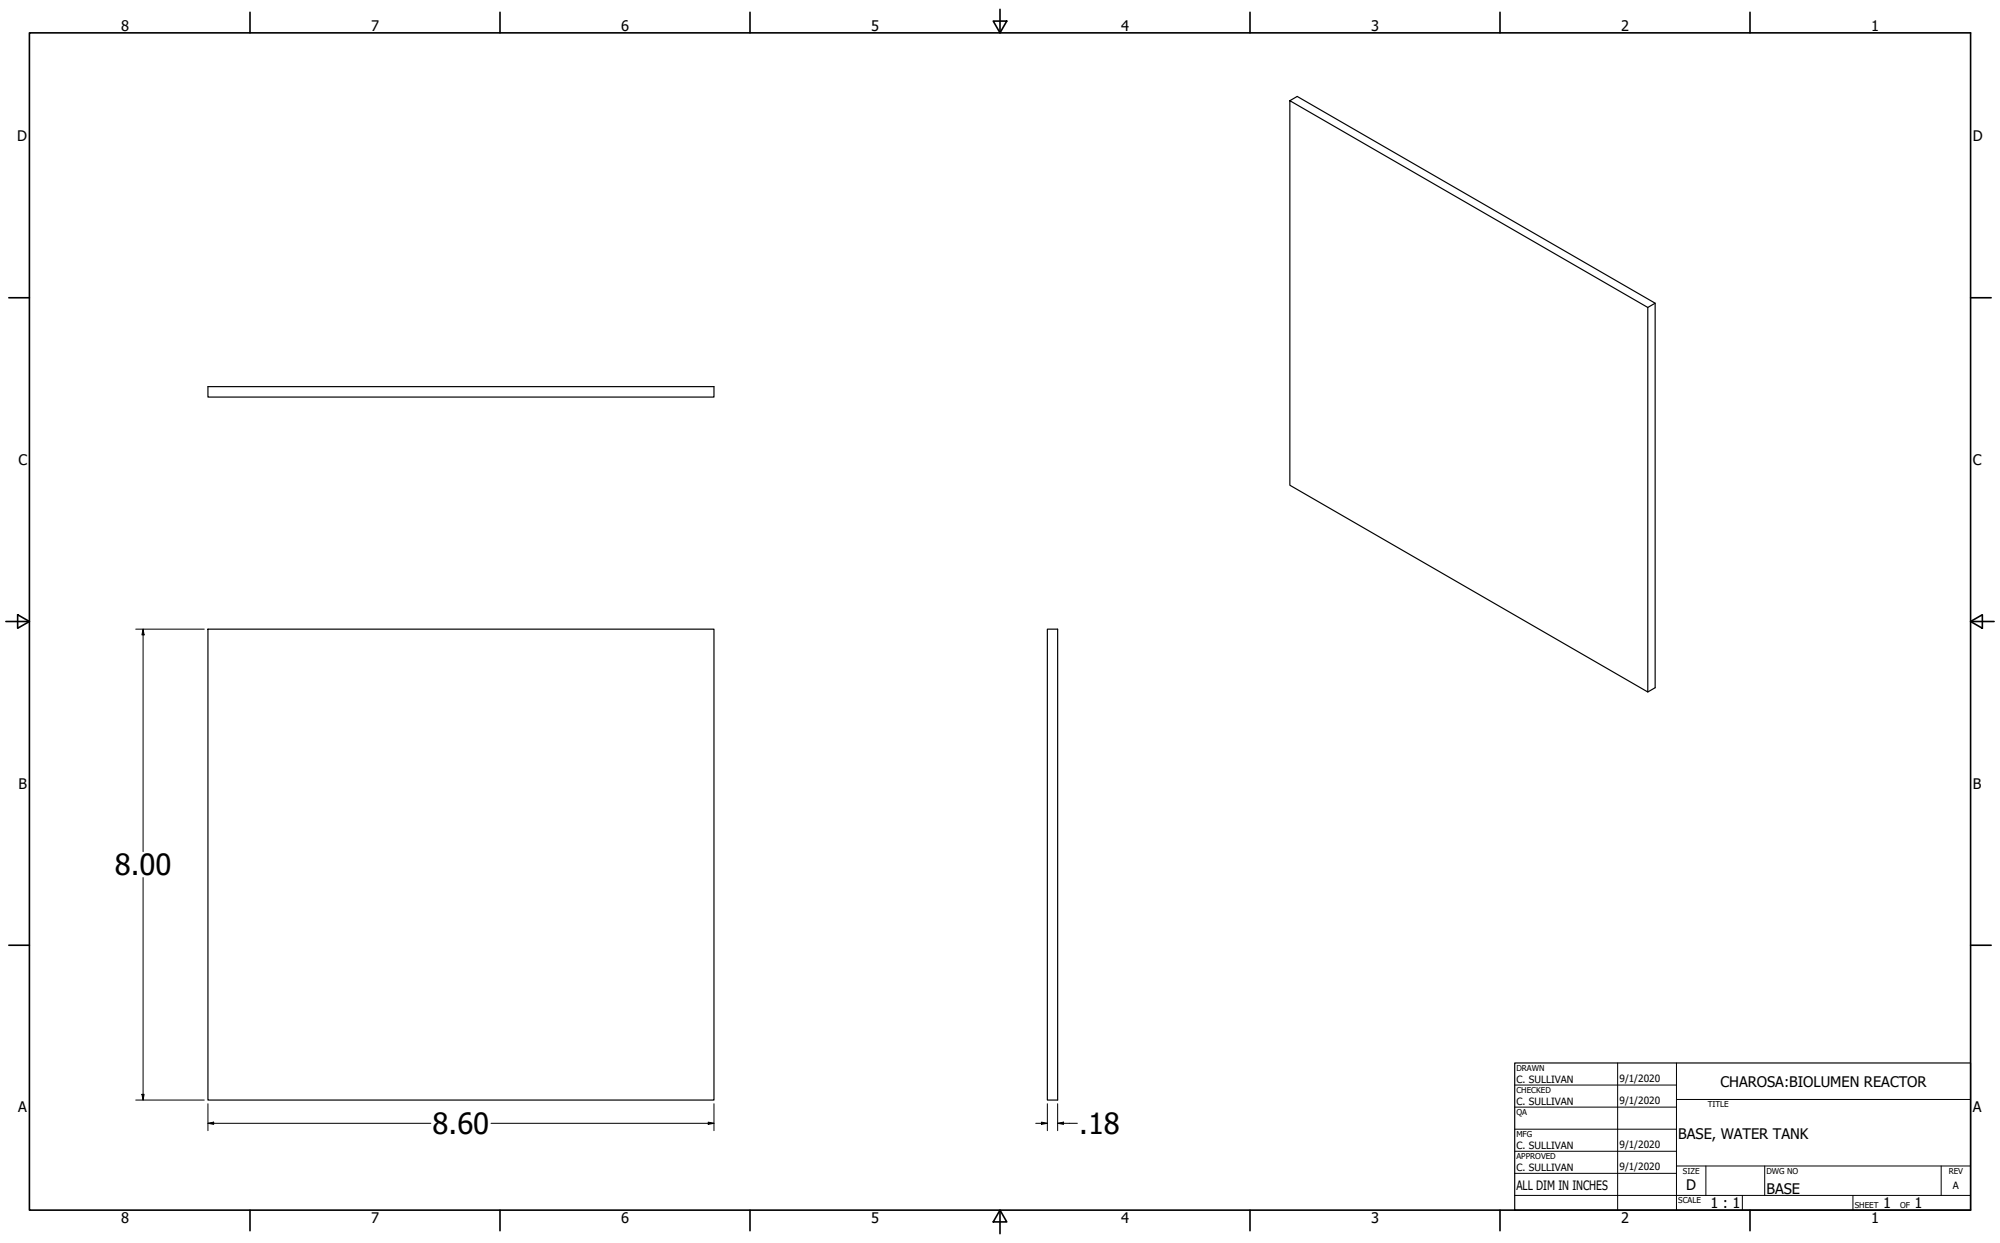
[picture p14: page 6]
DRAWN; CHECKED; MFG C. SULLIVAN; C. SULLIVAN; BASE; TITLE

CHAROSA:BIOLUMEN REACTOR

BASE, WATER TANK

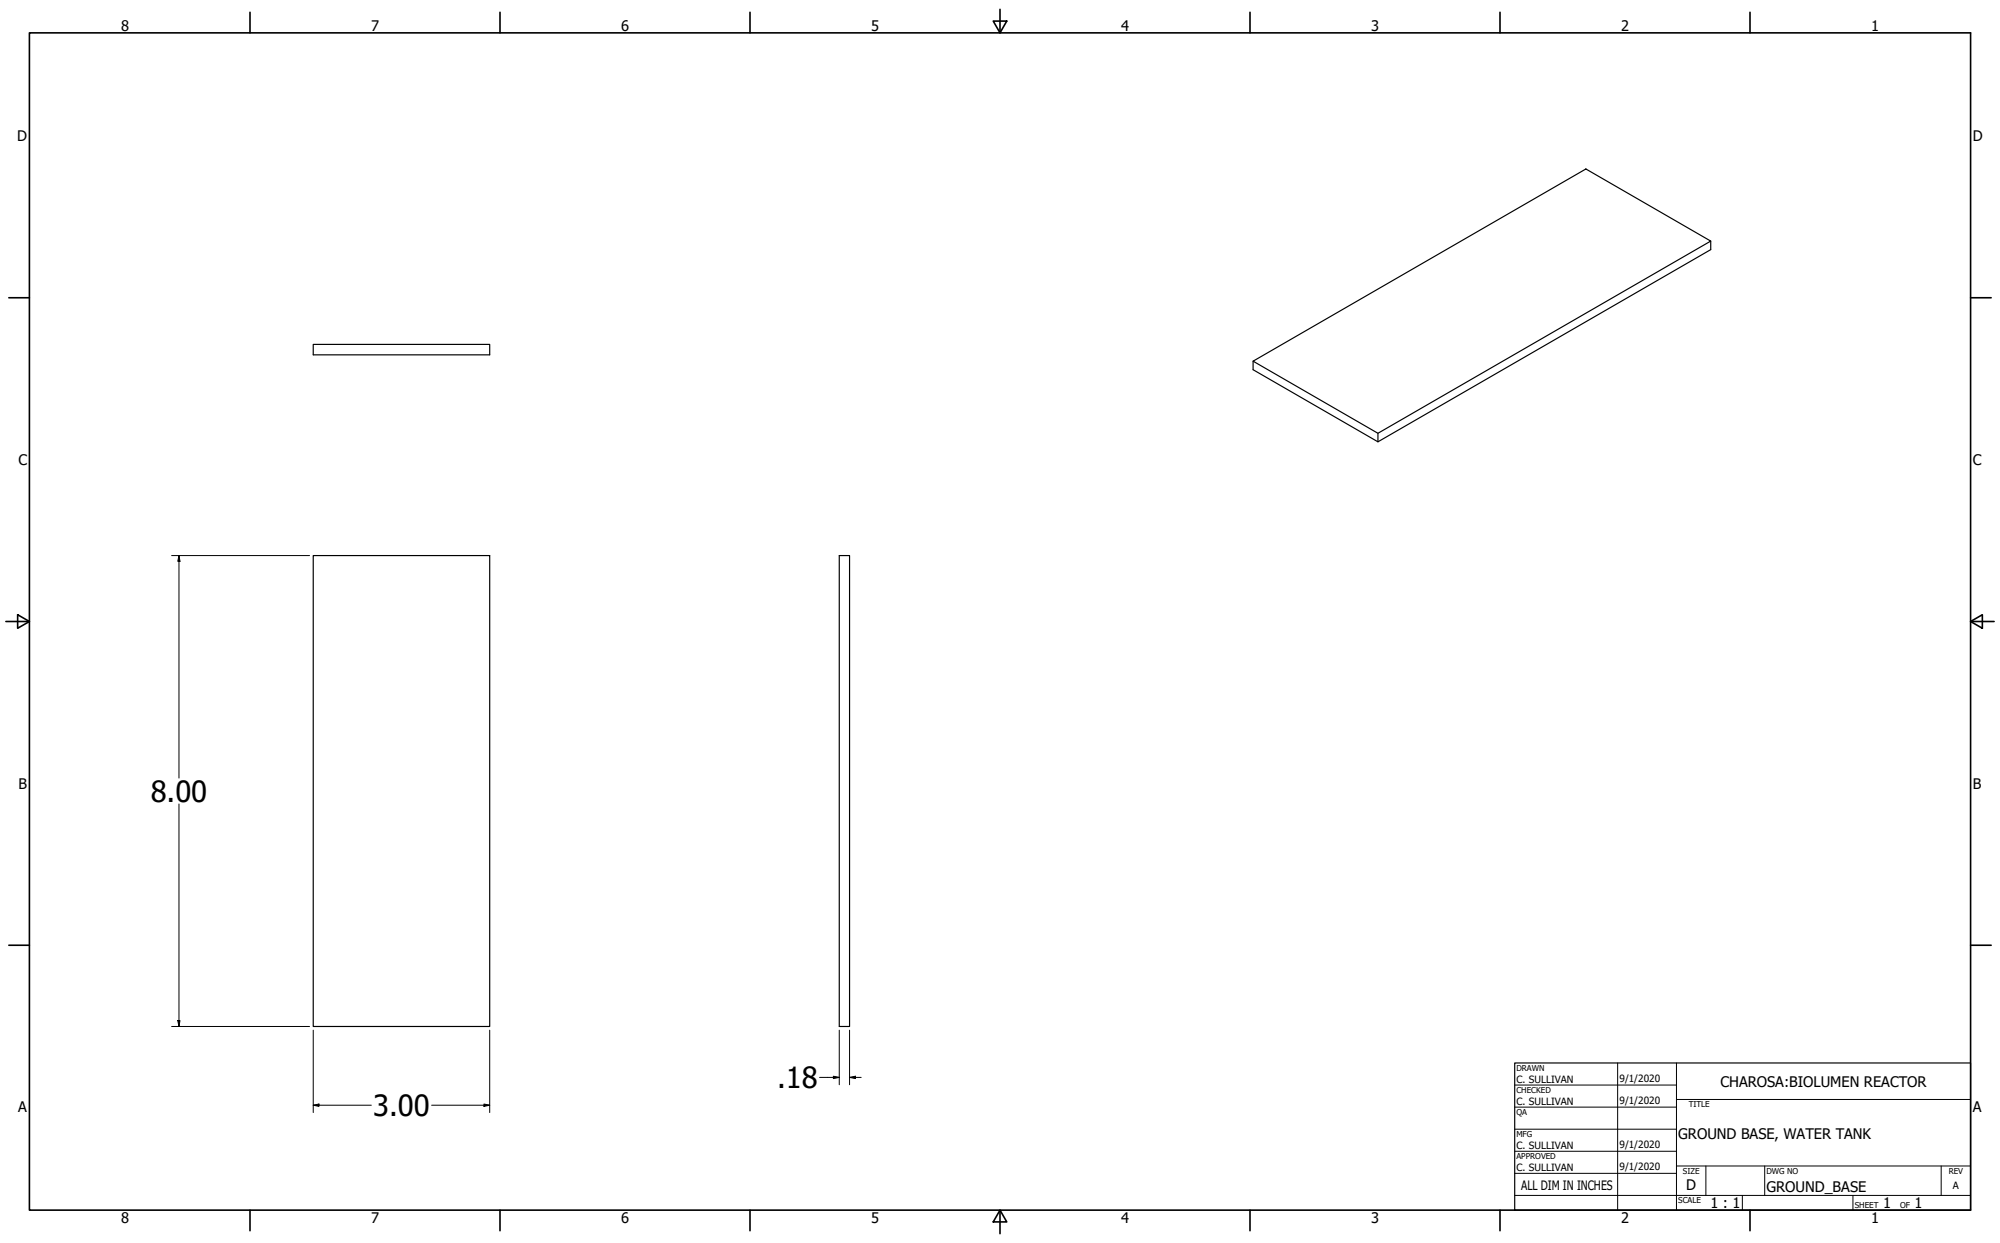
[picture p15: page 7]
DRAWN; CHECKED; MFG C. SULLIVAN; C. SULLIVAN; GROUND_BASE; TITLE

CHAROSA:BIOLUMEN REACTOR

GROUND BASE, WATER TANK

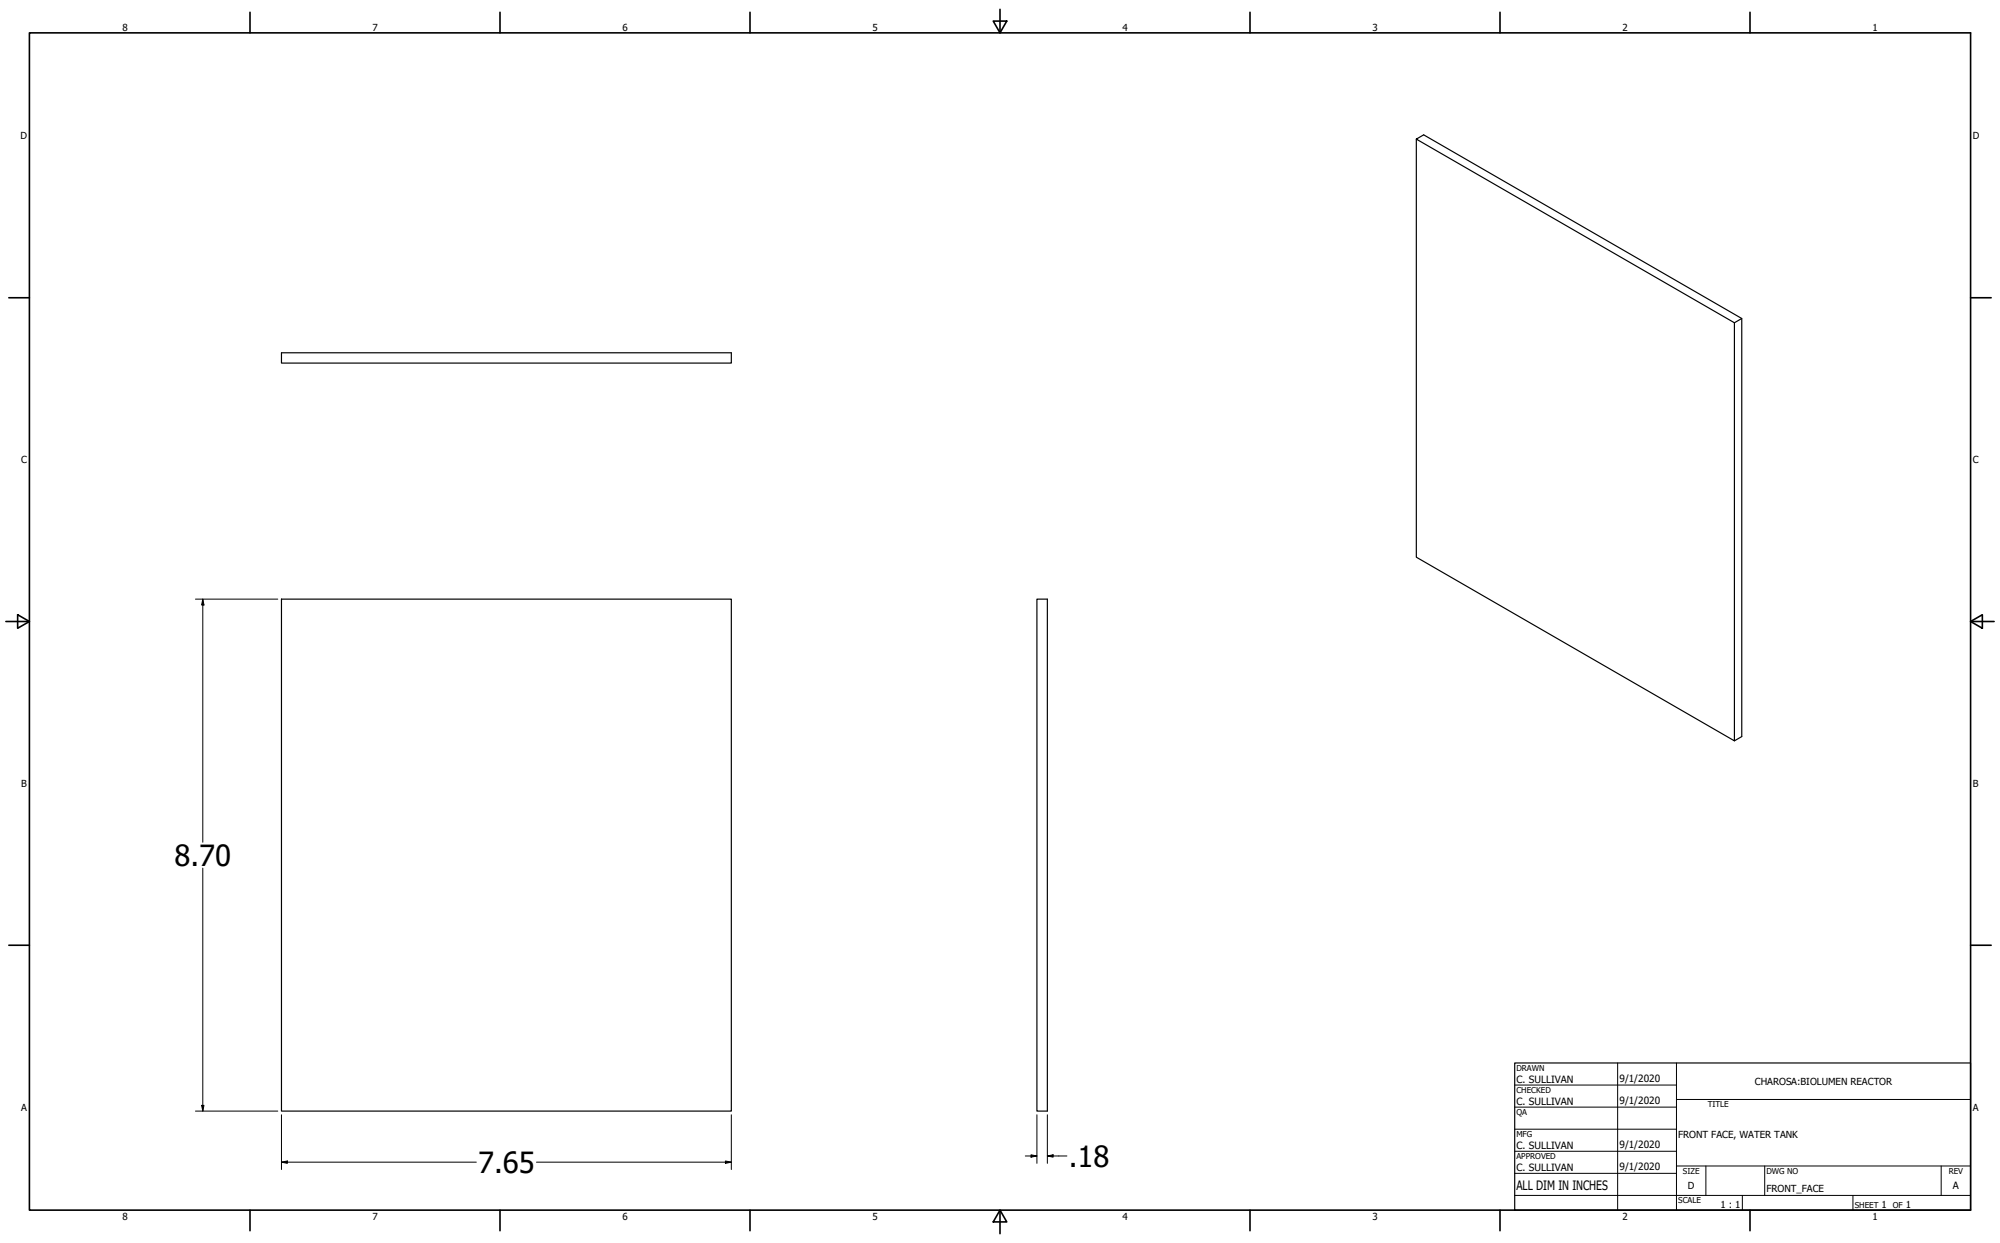
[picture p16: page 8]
DRAWN; CHECKED; MFG C. SULLIVAN; C. SULLIVAN; FRONT_FACE; TITLE

CHAROSA:BIOLUMEN REACTOR

FRONT FACE, WATER TANK

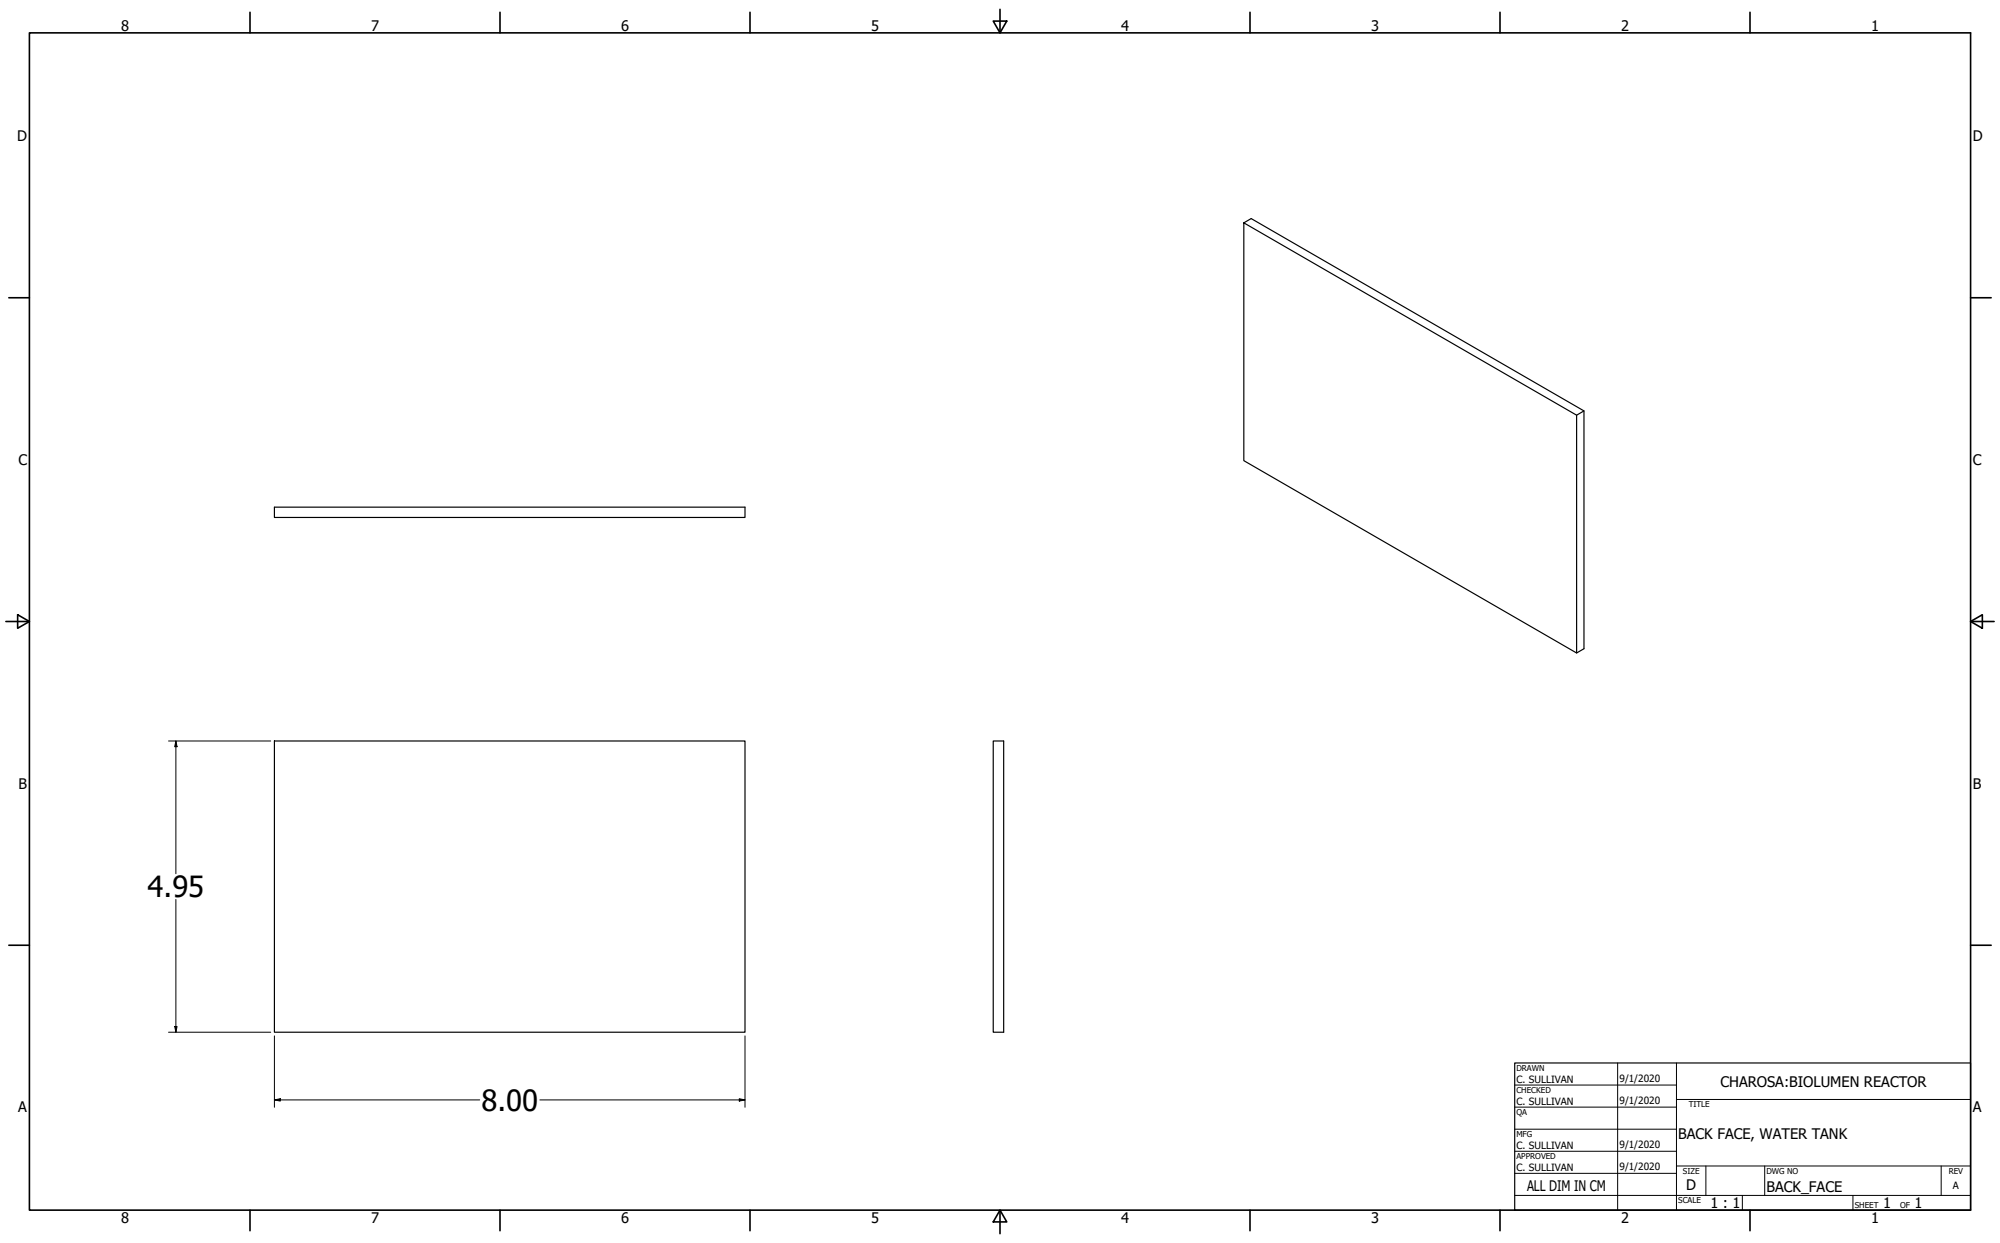
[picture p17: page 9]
DRAWN; CHECKED; MFG C. SULLIVAN; C. SULLIVAN; BACK_FACE; TITLE

CHAROSA:BIOLUMEN REACTOR

BACK FACE, WATER TANK

ALL DIM IN CM

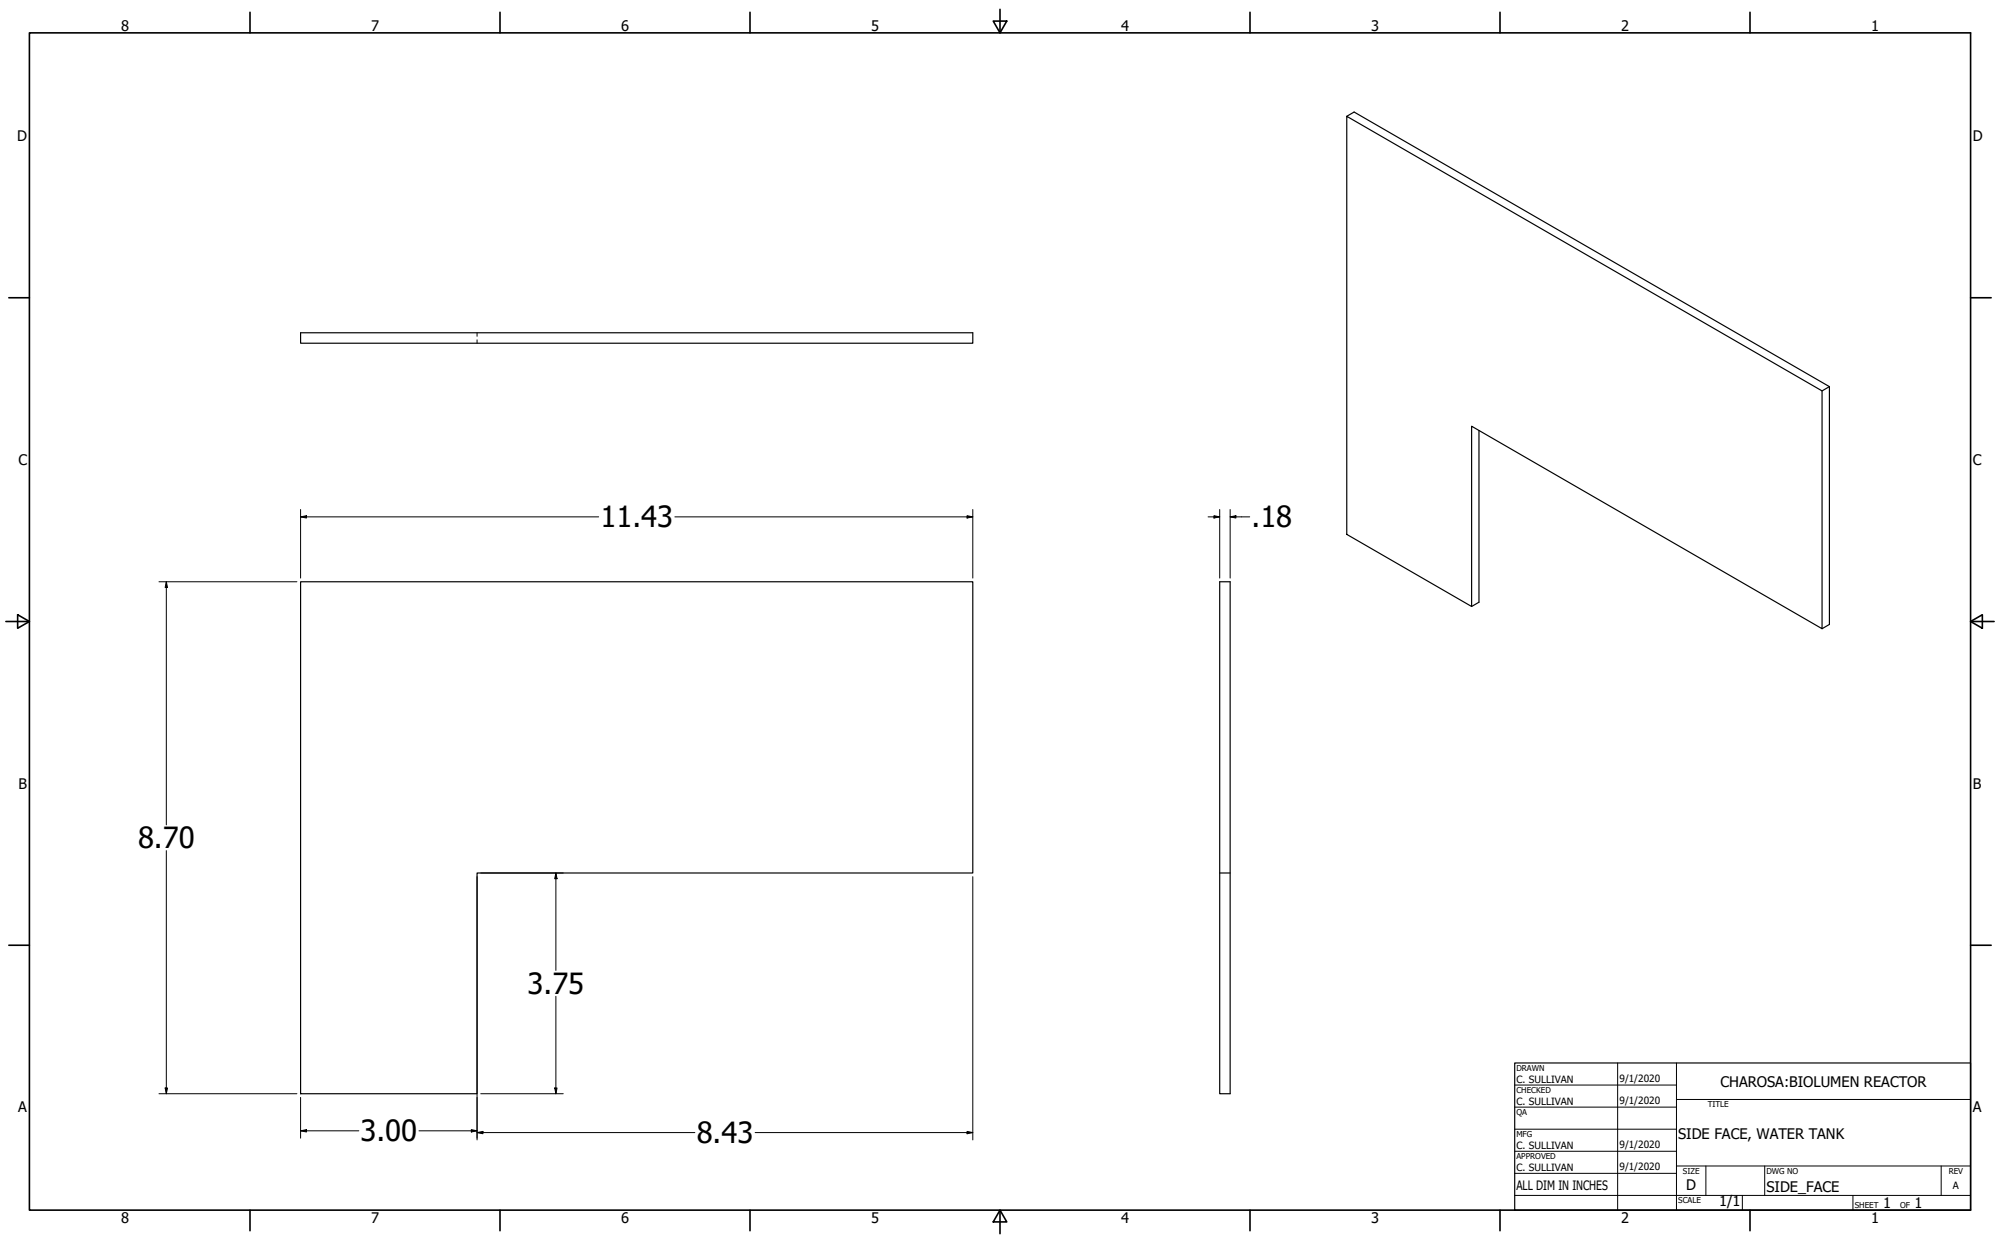
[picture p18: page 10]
DRAWN; CHECKED; MFG C. SULLIVAN; C. SULLIVAN; SIDE_FACE; TITLE

CHAROSA:BIOLUMEN REACTOR

SIDE FACE, WATER TANK

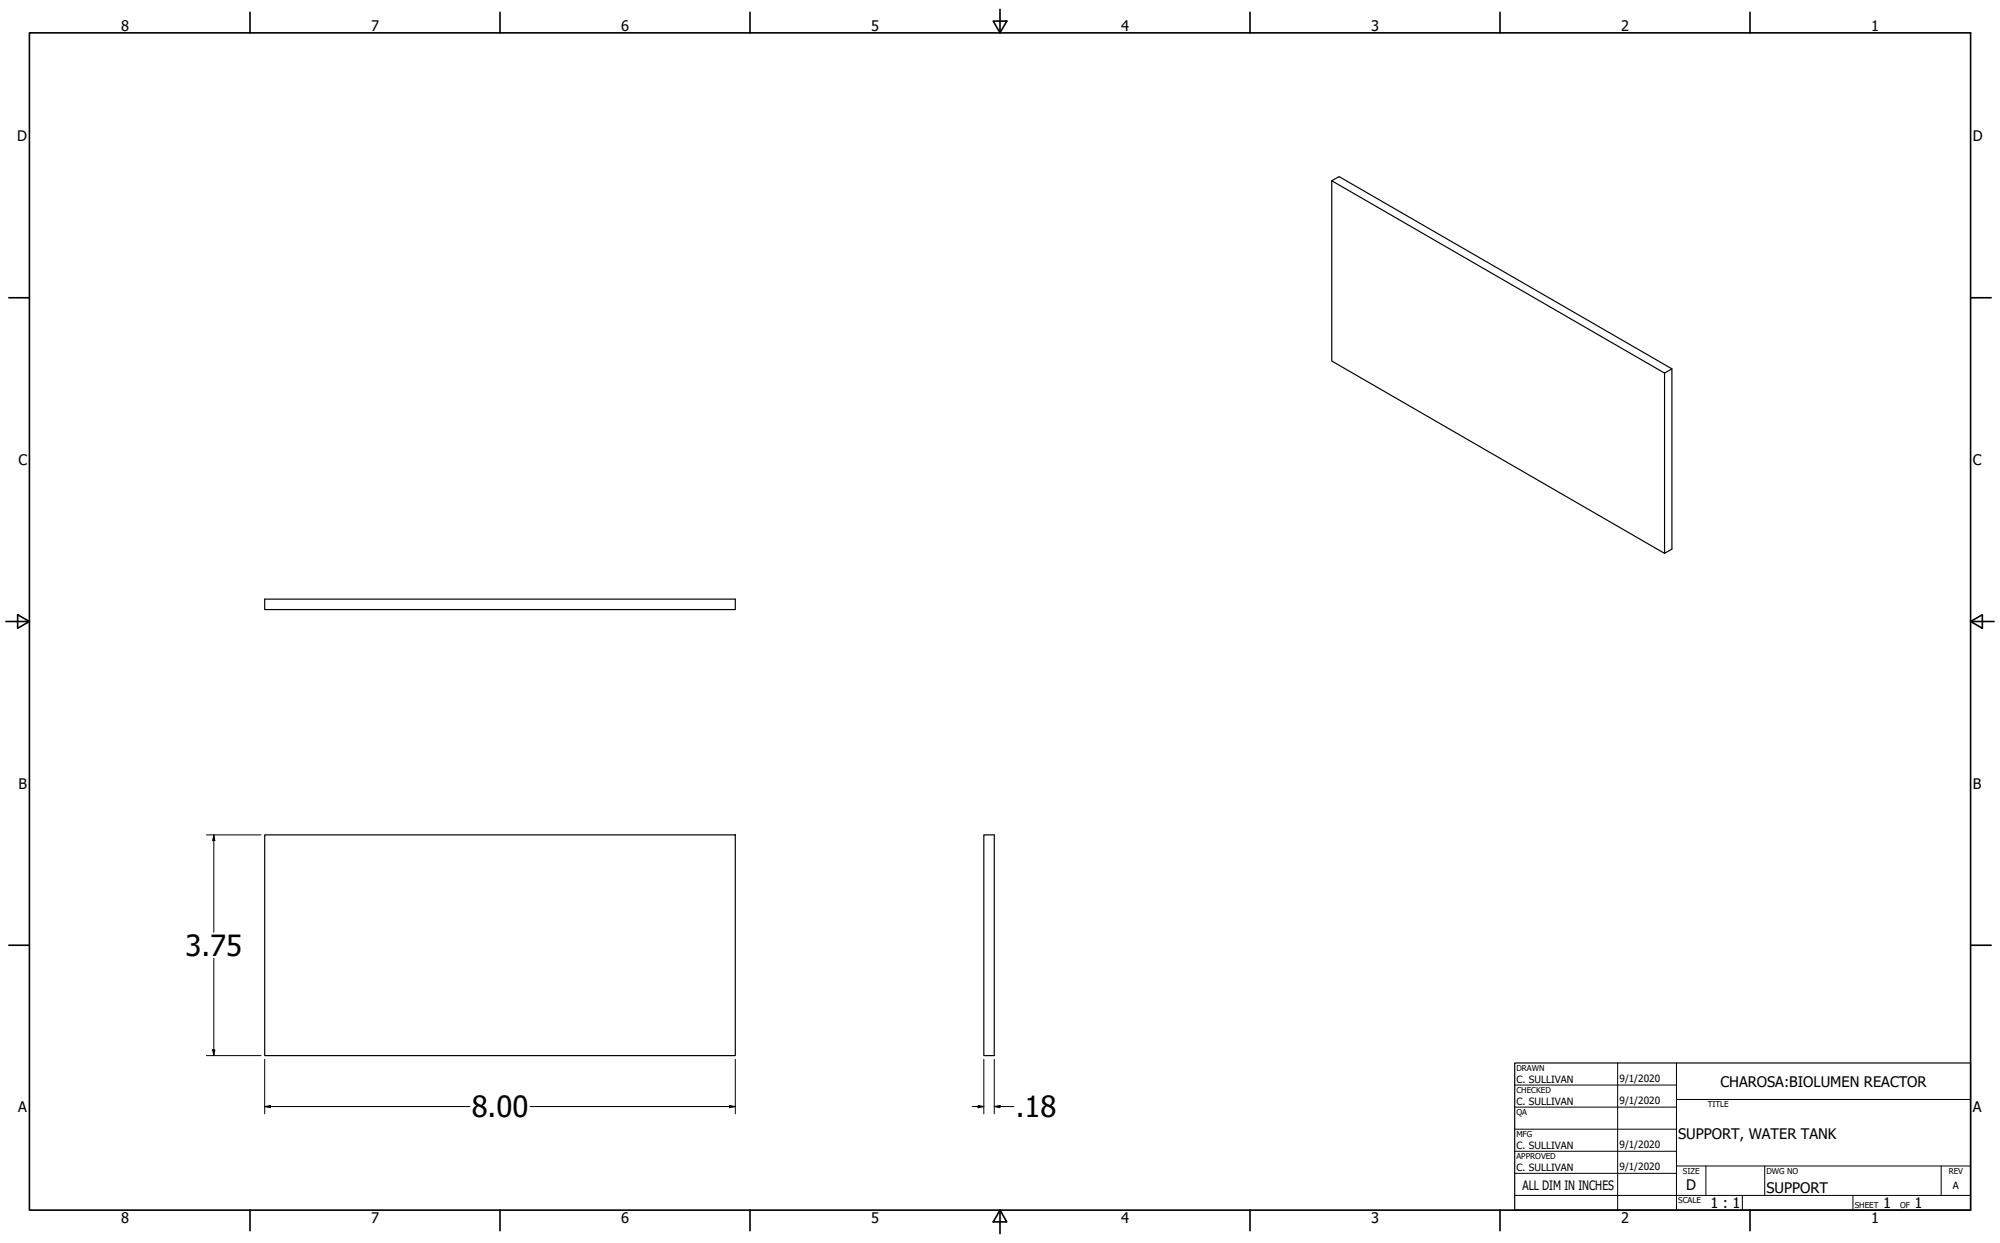
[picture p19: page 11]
DRAWN; CHECKED; MFG C. SULLIVAN; C. SULLIVAN; SUPPORT; TITLE

CHAROSA:BIOLUMEN REACTOR

SUPPORT, WATER TANK

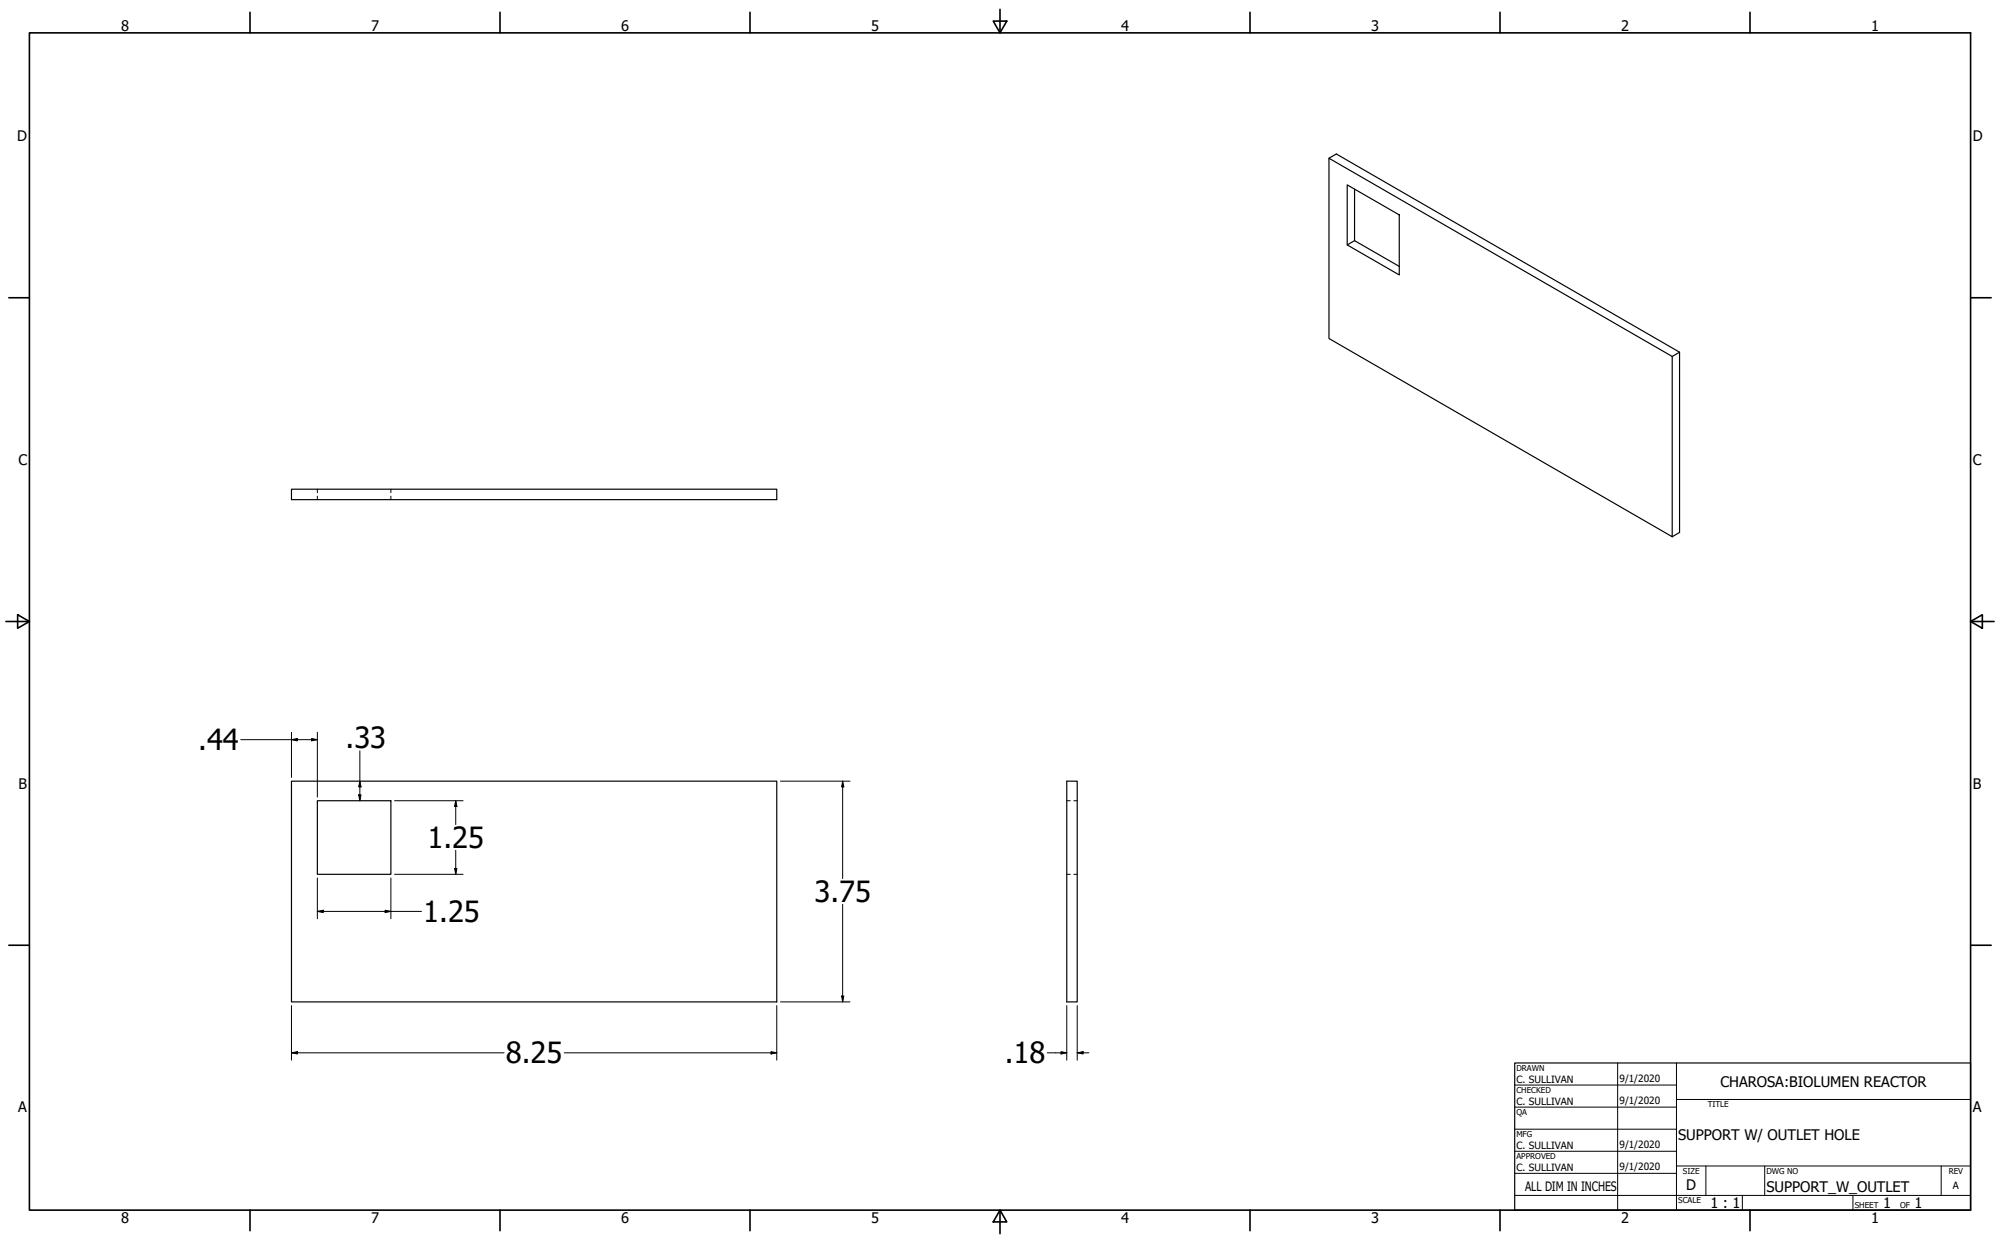
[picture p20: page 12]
DRAWN; CHECKED; MFG C. SULLIVAN; C. SULLIVAN; SUPPORT_W_OUTLET; TITLE

CHAROSA:BIOLUMEN REACTOR

SUPPORT W/ OUTLET HOLE

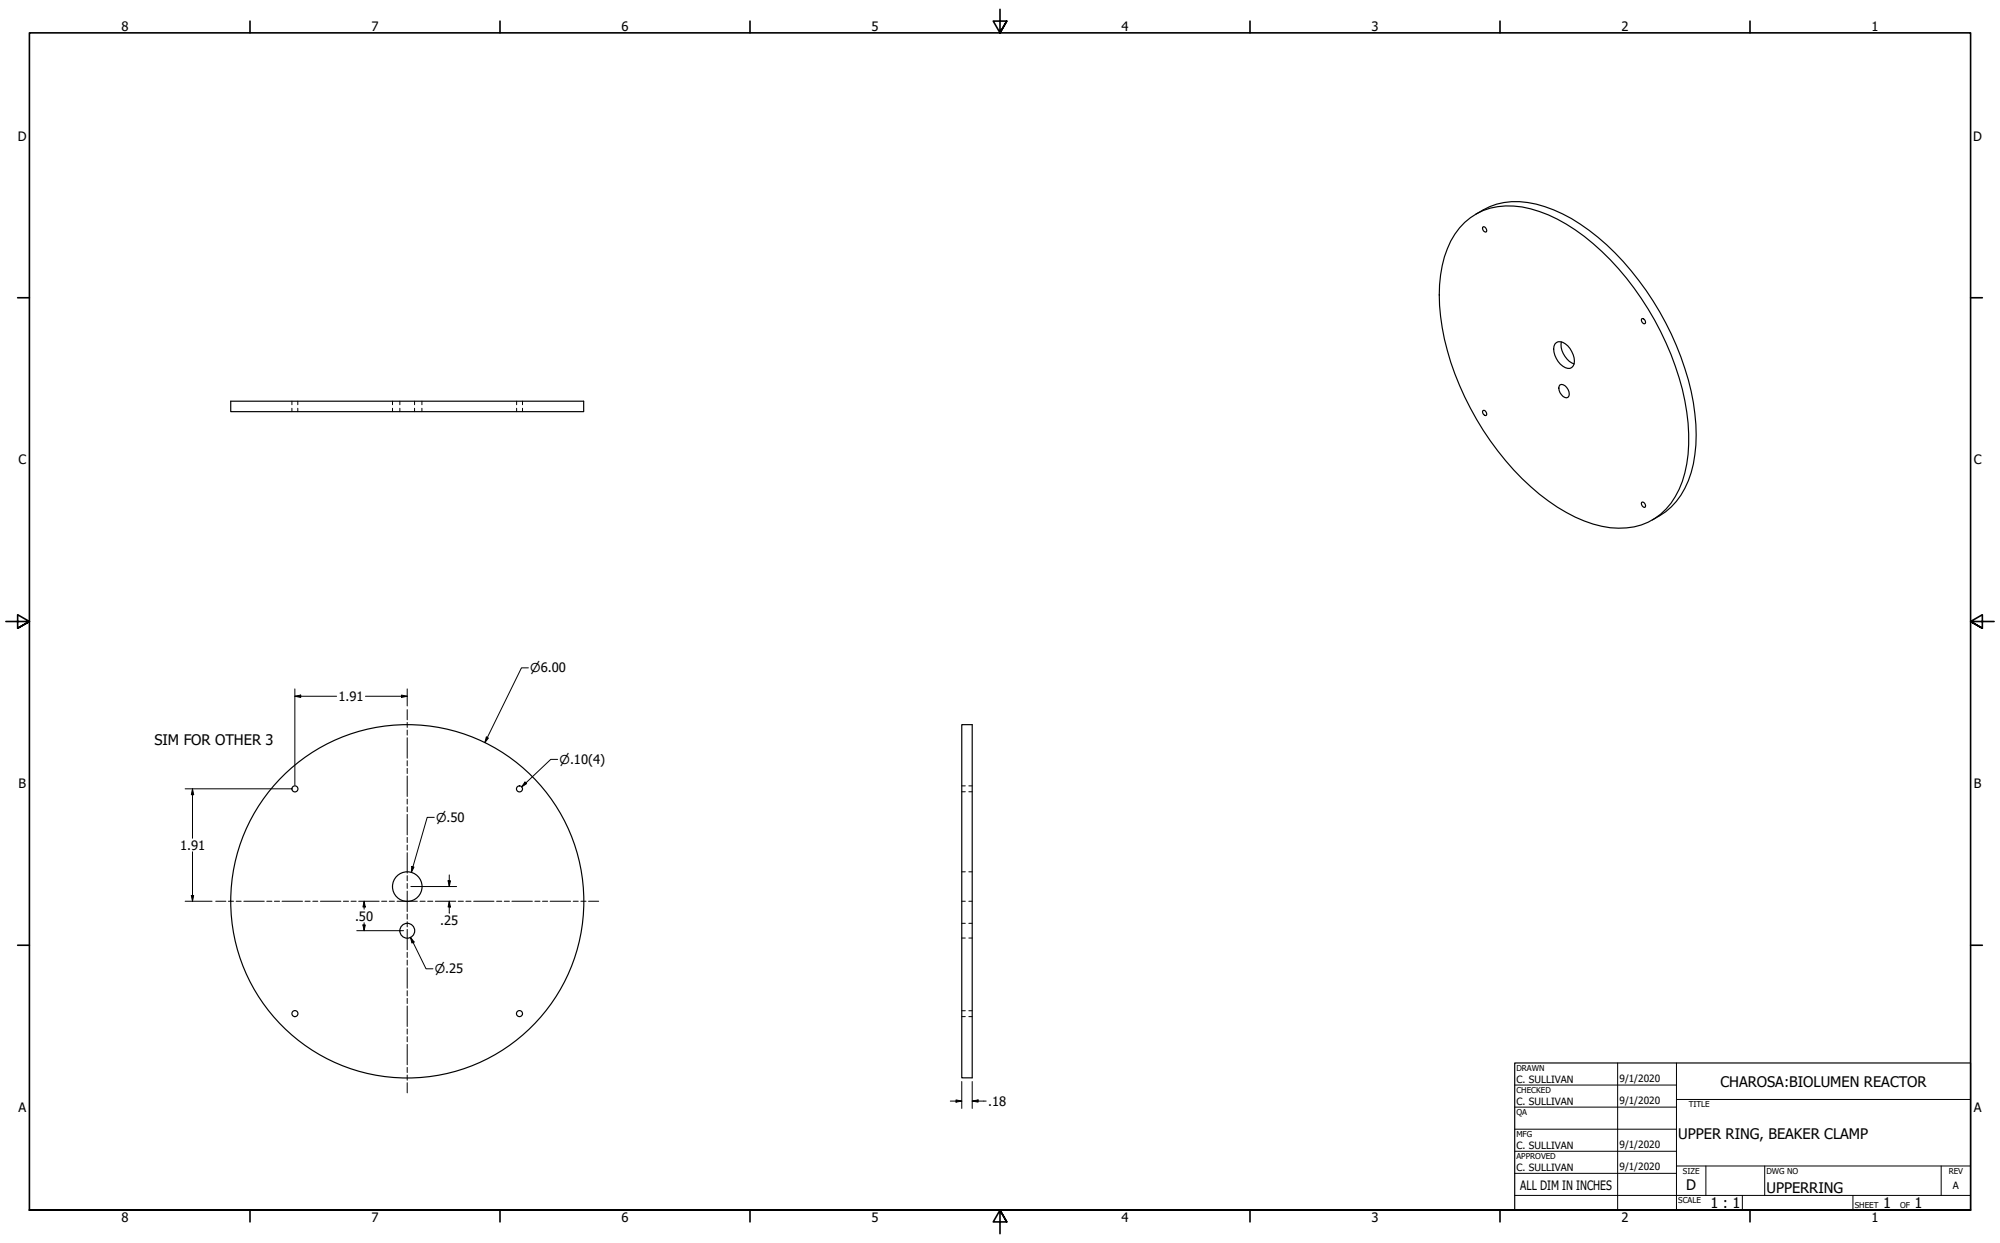
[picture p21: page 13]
DRAWN; CHECKED; MFG C. SULLIVAN; C. SULLIVAN; UPPERRING; TITLE

SIM FOR OTHER 3

CHAROSA:BIOLUMEN REACTOR

UPPER RING, BEAKER CLAMP

DRAWN; CHECKED; MFG C. SULLIVAN; C. SULLIVAN; LOWERRING1; TITLE; CHAROSA

LOWER RING 1, BEAKER CLAMP

DRAWN; CHECKED; MFG C. SULLIVAN; C. SULLIVAN; LOWERRING2; TITLE; CHAROSA:

LOWER RING 2, BEAKER CLAMP

DRAWN; CHECKED; MFG C. SULLIVAN; C. SULLIVAN; LOWERRING3; TITLE

CHAROSA:BIOLUMEN REACTOR

LOWER RING 3, BEAKER CLAMP

DRAWN; CHECKED; MFG C. SULLIVAN; C. SULLIVAN; GASKET; TITLE

CHAROSA:BIOLUMEN REACTOR

GASKET, CLAMPING RING

P.22

DRAWN; CHECKED; MFG C. SULLIVAN; C. SULLIVAN; PLASTIC_LATCH; TITLE

CHAROSA:BIOLUMEN REACTOR

PLASTIC LATCH, BEAKER

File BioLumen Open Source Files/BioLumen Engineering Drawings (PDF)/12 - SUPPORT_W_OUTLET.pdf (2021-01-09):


DRAWN C. SULLIVAN | 9/1/2020 | CHAROSA:BIOLUMEN REACTOR

CHECKED C. SULLIVAN | 9/1/2020

MFG C. SULLIVAN | 9/1/2020

SUPPORT W/ OUTLET HOLE

APPROVED C. SULLIVAN | 9/1/2020

SIZE D | DWG NO SUPPORT_W_OUTLET | REV A

ALL DIM IN INCHES

SCALE 1 : 1 | SHEET 1 OF 1

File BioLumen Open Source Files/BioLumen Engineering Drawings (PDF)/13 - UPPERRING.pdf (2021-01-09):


SIM FOR OTHER 3

DRAWN C. SULLIVAN | 9/1/2020 | CHAROSA:BIOLUMEN REACTOR

CHECKED C. SULLIVAN | 9/1/2020

UPPER RING, BEAKER CLAMP

MFG C. SULLIVAN | 9/1/2020

APPROVED C. SULLIVAN | 9/1/2020

SIZE D | DWG NO UPPERRING | REV A

ALL DIM IN INCHES

SCALE 1 : 1 | SHEET 1 OF 1

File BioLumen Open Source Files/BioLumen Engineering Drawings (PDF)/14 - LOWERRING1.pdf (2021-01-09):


DRAWN C. SULLIVAN | 9/1/2020 | CHAROSA

CHECKED C. SULLIVAN | 9/1/2020

LOWER RING 1, BEAKER CLAMP

MFG C. SULLIVAN | 9/1/2020

APPROVED C. SULLIVAN | 9/1/2020

SIZE D | DWG NO LOWERRING1 | REV A

SCALE 1 : 1 | | SHEET 1 OF 1

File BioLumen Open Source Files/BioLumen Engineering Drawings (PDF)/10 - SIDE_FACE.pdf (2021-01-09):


DRAWN C. SULLIVAN | 9/1/2020 | CHAROSA:BIOLUMEN REACTOR

CHECKED C. SULLIVAN | 9/1/2020

SIDE FACE, WATER TANK

MFG C. SULLIVAN | 9/1/2020

APPROVED C. SULLIVAN | 9/1/2020

SIZE D | DWG NO SIDE_FACE | REV A

ALL DIM IN INCHES

1/1 SCALE | SHEET 1 OF 1

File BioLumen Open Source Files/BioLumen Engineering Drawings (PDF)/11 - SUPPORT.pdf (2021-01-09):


DRAWN C. SULLIVAN | 9/1/2020 | CHAROSA:BIOLUMEN REACTOR

CHECKED C. SULLIVAN | 9/1/2020

SUPPORT, WATER TANK

MFG C. SULLIVAN | 9/1/2020

APPROVED C. SULLIVAN | 9/1/2020

SIZE D | DWG NO SUPPORT | REV A

ALL DIM IN INCHES

SCALE 1 : 1 | SHEET 1 OF 1

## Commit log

2019-04-22 Adding board layout and main script
    [BioLumen.fzz]
2019-04-22 Added png of board
2019-04-29 Update BioLumen.py
    - Added conversion from analog to voltage
    - Added conversion from voltage to pH
2019-05-20 Added pump functionality
2019-05-20 Fixed pump bug
2019-05-22 Seperated pumps and temp sensor into different files
2019-05-30 Working on pi
    [data_file.csv]
2019-05-30 Added gitignore
    [data_file.csv]
2021-01-09 Adding open-source file directory
    [ASSY_CLAMPING_RING.iam, ASSY_CLAMPING_RING.idw, ASSY_REACTOR.iam, ASSY_REACTOR.idw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]
